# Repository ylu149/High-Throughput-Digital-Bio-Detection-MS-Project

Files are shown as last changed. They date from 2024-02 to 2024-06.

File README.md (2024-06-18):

# Automated High-Throughput Virus Detection System

## Project Demo
https://drive.google.com/file/d/1OpM7CCfLptdZOMjBMuT8S1R-RPZTFUh5/view?usp=sharing

## Introduction

In response to the growing threat of infectious diseases and viruses, especially in the post-COVID-19 era, there is an urgent need for cost-effective, multiplexed, label-free, high-throughput virus detection methods for small single samples. This project aims to design and prototype an automated system that can seamlessly transport and center a standardized microtiter plate's wells in front of a stationary Interferometric Reflectance Imaging Sensor (IRIS) optical system. The system facilitates high-throughput digital measurements of distinct binding events within each well, providing unprecedented sensitivity and resolution.

## Goals Outlined

The project is divided into three phases: research, prototyping, and testing. The research phase involves studying methods for positioning microtiter plates and exploring techniques for inserting IRIS chips into the plates. The findings are then used to create a 3D model of the design using SolidWorks. The prototyping phase optimizes the CAD model based on feedback and constructs a proof of concept. Finally, the testing phase focuses on reliability testing of the prototype assembly, including repeatability tests for plate positioning and evaluating the consistency of the dipping mechanism.

## Proposed Design

The proposed design integrates two systems: an XY positioning system and a dipping mechanism.

### XY Positioning System

The XY positioning system uses two pairs of rails and non-capacitive stepper motors to move a 96-well microtiter plate with high precision. The motors push the plate along two perpendicular axes, allowing the IRIS optical system to focus on the selected well. 

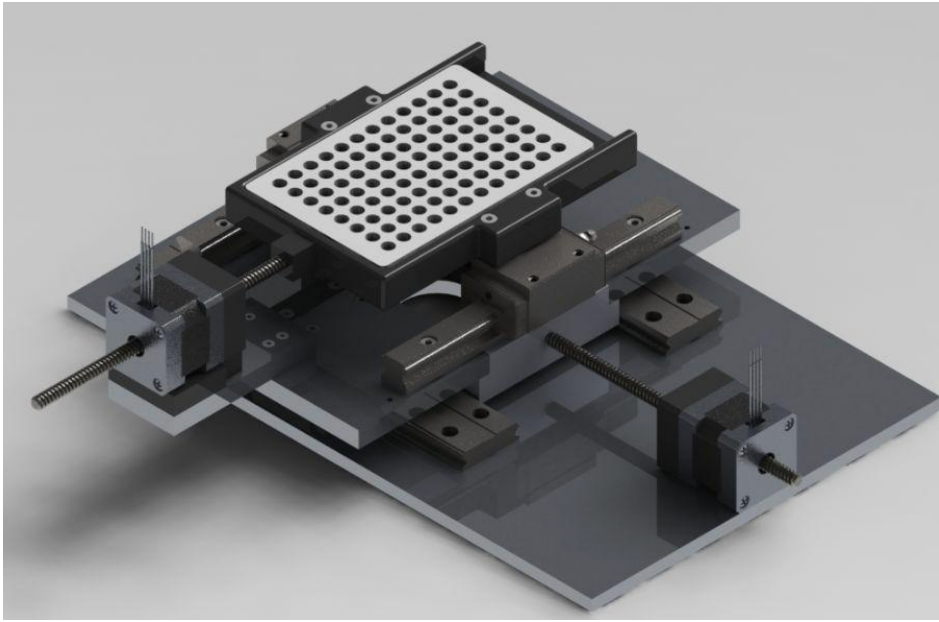
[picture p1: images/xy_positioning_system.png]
XY Positioning System


### Dipping Mechanism

The dipping mechanism facilitates the insertion and cleaning of IRIS chips in the microtiter plate. A specialized part called the "buckle" holds the IRIS chip and is attached to a 3D-printed holder with eight buckles, each equipped with springs to provide a cushion when the IRIS chip contacts the microtiter plate. A linear actuator facilitates the insertion and retraction of the IRIS chips. The entire assembly is illustrated below.

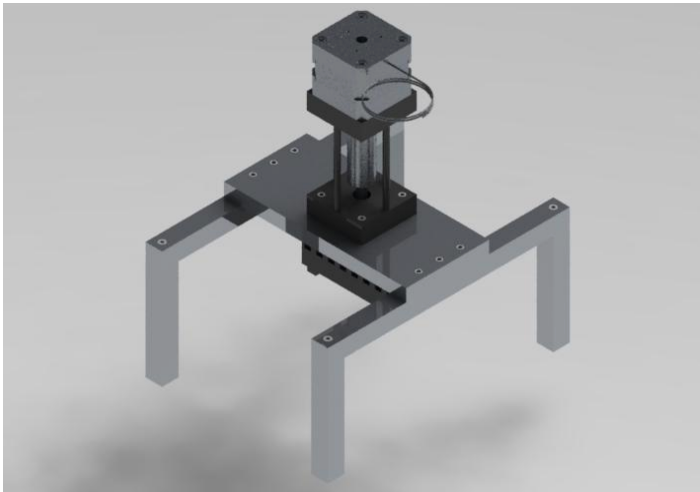
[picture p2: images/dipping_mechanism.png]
Dipping Mechanism


## Cleaning IRIS Chips

To clean the IRIS chips, half of the wells in the microtiter plate are designated for cleaning, while the other half is used for sampling. This arrangement allows the system to sequentially sample eight samples in a column, clean itself, and then proceed to resample.

## System Overview

The complete system, comprising the XY positioning system and dipping mechanism, is depicted below.

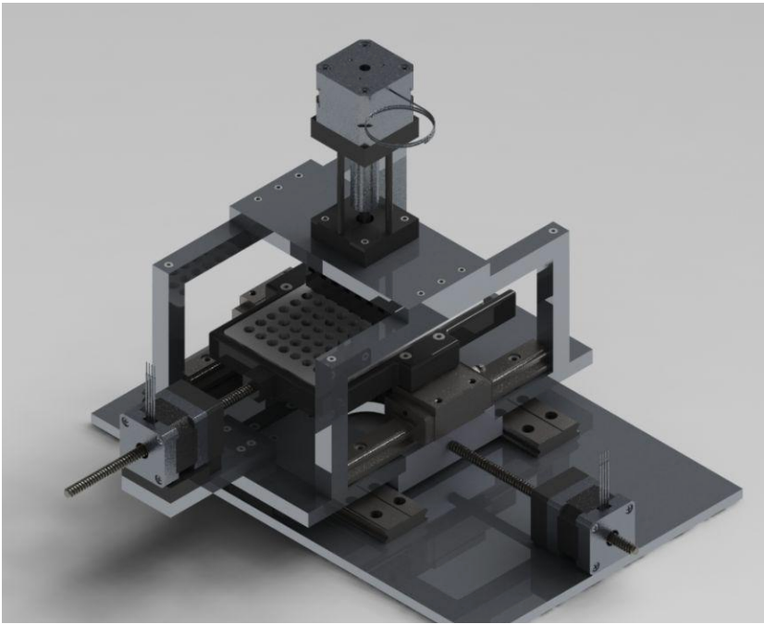
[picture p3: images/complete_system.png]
Complete System


## Arduino Wiring Diagram
The electrical system showing how the stepper motors are wired is shown below. Note each stepper motor, gets it's own Arduino and driver. 

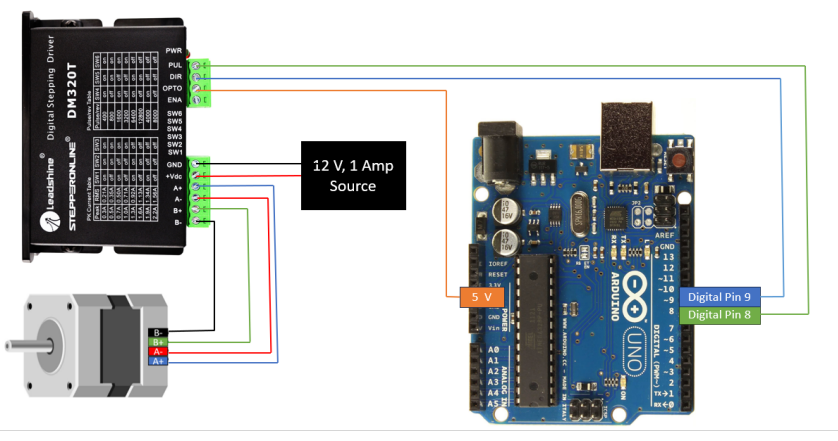
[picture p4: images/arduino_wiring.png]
Wiring Diagram


## Credits
- Harisson Cao: For being my partner throughout this project. 
- Andrew Gentile: For providing feedback as an engineer in industry. 
- The anonymous machinist who helped machine parts and gave GD&T feedback.
- Selim Unlu: For being the advising professor on this project.
- Mete Aslan: For the feedback he provided as a PhD student.  

## For more detailed explanations please refer to the report.pdf and BOM.XLSX documents.

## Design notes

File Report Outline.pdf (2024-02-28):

## Boston University College of Engineering Department of Electrical and Computer Engineering

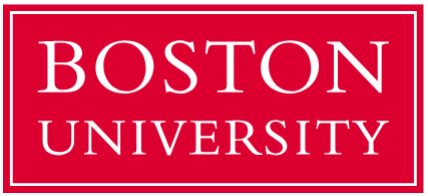
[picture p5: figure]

## High-Throughput Digital Biodetection

## Master’s Project End of Semester Report

## Harrison Cao & Yang Zeng Lu

## Advisor: Professor M. Selim Ünlü

## December 15th

, 2023

## Table of Contents

### I. Introduction | 3

### II. Goals Outlined | 3

### III. Proposed Design... | 4

### IV. Testing & Results | 8

### V. Conclusion | 10

### VI. Appendix | 12

### I. Introduction

Considering the growing threat posed by infectious diseases and viruses, particularly in light of

the post-Covid-19 era, there is an urgent and pressing need for cost-effective multiplexed, label-free,

high-throughput virus detection methods for small single samples. One emerging method for single

molecule detection involves harnessing optics through Interferometric Reflectance Imaging Sensors (IRIS

chips) to precisely gauge the size and quantity of particles within individual samples.

The objective of this project is to design and prototype an automated system capable of

seamlessly transporting and centering a standardized microtiter plate’s wells in front of a stationary IRIS

optical system. This system will facilitate high-throughput digital measurements of distinct binding events

within each well of a microtiter plate during the sample incubation process. This innovative approach

unlocks unprecedented capabilities in high-throughput digital bio-sensing, offering levels of sensitivity

and resolution that surpass traditional labeling methods.

### II. Goals Outlined

During the initial project proposal, the approach and subsequent goals were divided into three

phases: research, prototyping, and testing. In the research phase, various methods for positioning 96-well

microtiter plates while minimizing vibration were studied. Different techniques for inserting IRIS chips

into the 96-well microtiter plates were also explored. The concepts derived from this research were then

used to create a 3D model of the design using SolidWorks. During the prototyping phase, we optimized

the CAD model based on feedback received. This optimized design was then constructed as a proof of

concept. Finally, in the testing phase, we focused on the reliability testing of the prototype assembly. This

involved conducting repeatability tests for positioning the microtiter plates along two different axes and

evaluating the consistency of our dipping mechanism.

### III. Proposed Design

The proposed design for this project involves two systems integrated together. These systems

include a XY positioning system and the dipping mechanism.

The objective of the XY positioning system is to move a 96-well microtiter plate with high

precision and accuracy from well to well. Specifically, the system should position a designated well, as

selected by the user, to a focal point in a 2D space. This positioning enables the IRIS optical system to

focus on the selected well.

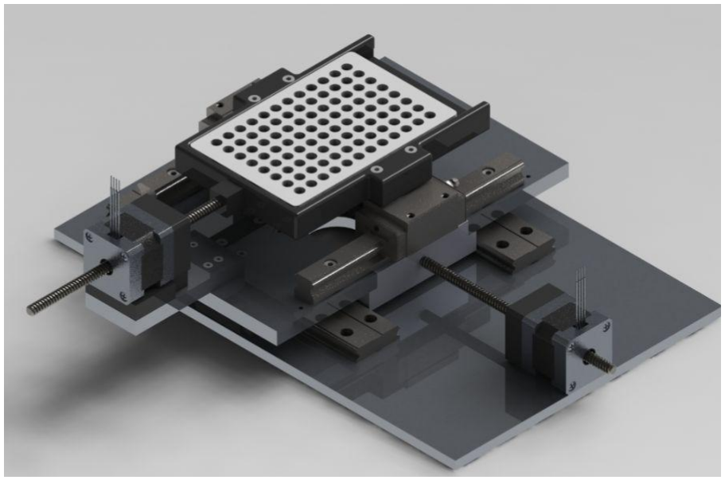
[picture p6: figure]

Figure 1: 3D Render of XY Positioning System in SolidWorks

The proposed design for positioning the microtiter plate uses two pairs of rails and two

non-capacitive stepper motors. These motors will position the microtiter plates by pushing them along

two perpendicular axes, with each axis having its own set of rails. By pushing the well plate only from its sides, it is ensured that the bottom of the wells remains unobstructed. This design allows the IRIS optics

system to capture the individual wells of the microtiter plate as the positioning system moves the plate.

Additionally, an Arduino, alongside a stepper motor driver, will be used to control the

non-capacitive stepper motors. The wiring diagram for this setup is shown in figure 2. The pseudo-code

for driving the stepper motor can be found in the appendix.

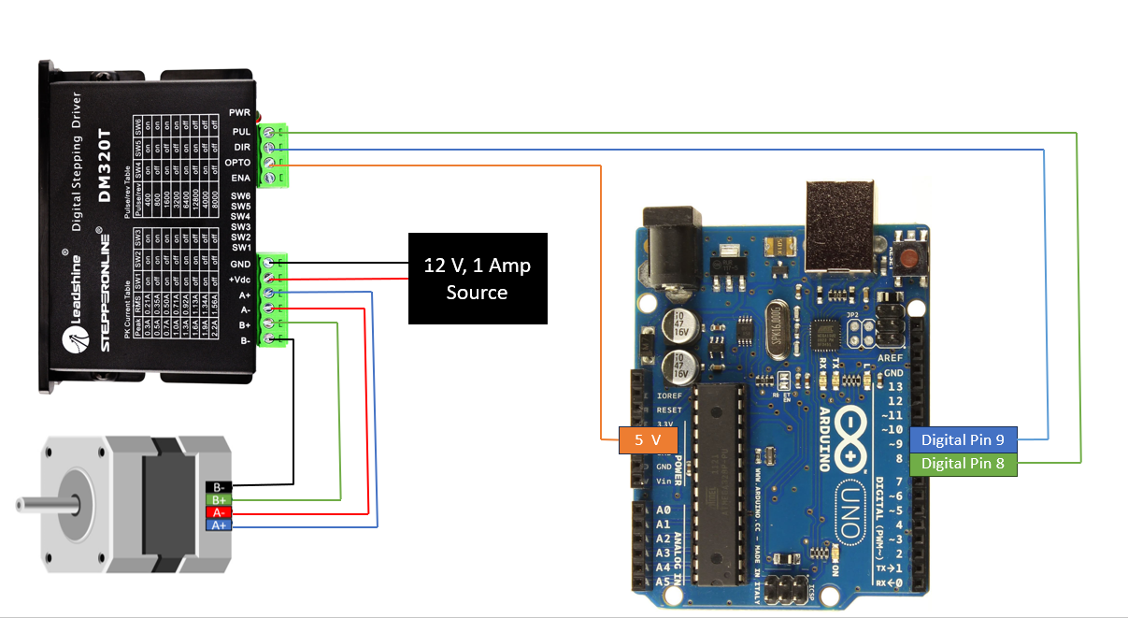
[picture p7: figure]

Figure 2: Wiring diagram for Arduino, stepper motors, and stepper motor drivers

To facilitate the insertion and cleaning of IRIS chips in a microtiter plate for the IRIS optical

system, a specialized dipping mechanism needed to be designed. This mechanism ensures the IRIS chips

are held securely and make direct contact with the base of the microtiter plate, without causing damage to

either component. The IRIS chip must be positioned no more than 0.5 mm from the inside glass surface of

the well plate for the optical system to function effectively. Additionally, to prevent cross-contamination

between samples, a cleaning method for the IRIS chips after each sample is necessary.

Addressing these requirements, the proposed solution involves a resin-printed part called the

"buckle," to which the IRIS chip will be friction-fitted to. This buckle will then be attached to a

3D-printed holder alongside eight other buckles, each equipped with springs. These springs provide a 2

mm cushion when the IRIS chip contacts the microtiter plate, protecting the glass at the bottom of the

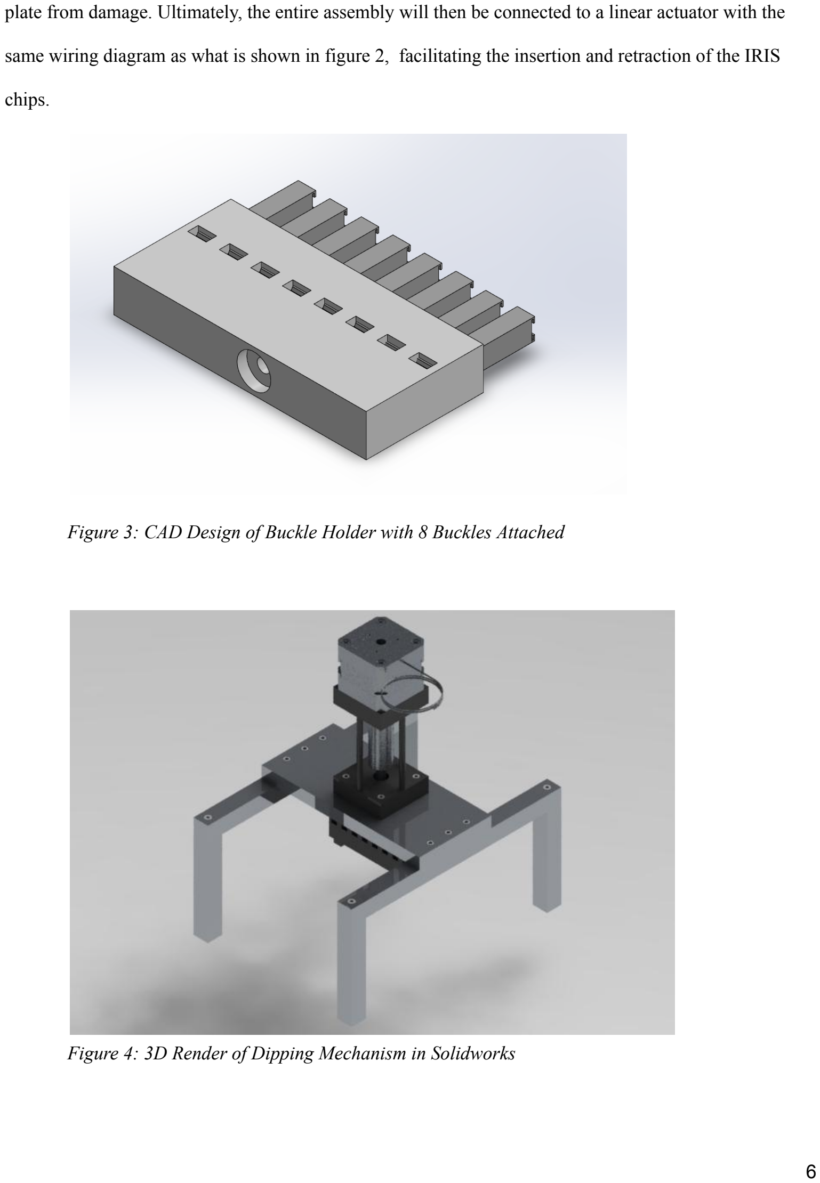
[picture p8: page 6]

plate from damage. Ultimately, the entire assembly will then be connected to a linear actuator with the

same wiring diagram as what is shown in figure 2, facilitating the insertion and retraction of the IRIS

chips.

Figure 3: CAD Design of Buckle Holder with 8 Buckles Attached

Figure 4: 3D Render of Dipping Mechanism in Solidworks

For cleaning the IRIS chips, it's proposed that half of the wells in the microtiter plate be

designated for cleaning, while the other half are used for sampling. This arrangement allows the device to

sequentially sample eight samples in a column, clean itself, and then proceed to resample.

Ultimately, our entire system is shown below in figure 5. A bill of materials can be found in the

Appendix

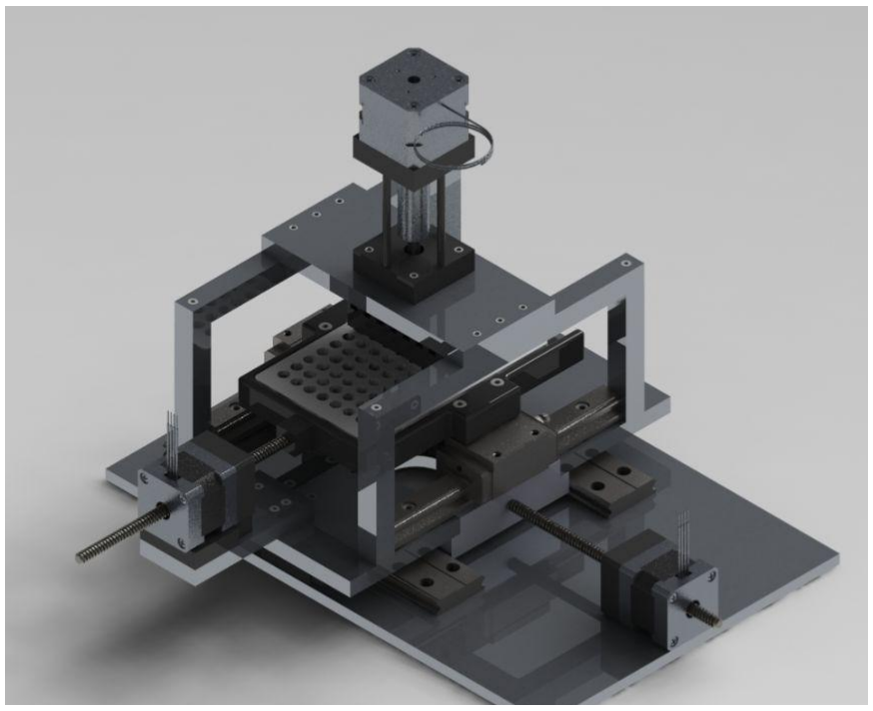
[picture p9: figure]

Figure 5: 3D Render of the XY Positioning and Dipping System in SolidWorks

### IV. Testing & Results

To evaluate the precision and accuracy of the XY positioning system, each axis was assessed

independently. The x-axis, controlled by the stepper motor pushing on the shorter edge of the microtiter

plate, determines the positioning of rows, labeled A-F. Conversely, when the motor pushes along the

longer edge or the y-axis, it positions the columns of the microtiter plate, each labeled with a number

labeled 1-12.

For specific cell positioning tests on the microtiter plate, the X and Y axes were individually

examined using a consistent method. Regarding the X-axis, an arbitrary zero point was established to

align row A with the hole for the optical system. After setting this point, the distance traveled between

rows was measured ten times. The process involved commanding the stepper motor to move sequentially

from row A to H. Upon reaching row H, the plate returned to A for repeated measurements. These tests

were conducted ten times, and the resulting data was used to calculate the standard deviation, reflecting

the precision of the X-axis positioning system. For accuracy assessment, the average deviation from each

row was determined. This value, along with the known 9 mm ground truth value, was used to calculate

the average percentage error. Please refer to table 1 below for the values. Overall, there is less than a 0.1

mm standard deviation and less than 2% error for moving the stepper motor.

Rows | A | B | C | D | E | F | G | H
Average (mm) | 19.51 | 28.51 | 37.53 | 46.447 | 55.36 | 64.32 | 73.17 | 82.14
Standard Deviation (mm) | 0.077 | 0.044 | 0.040 | 0.047 | 0.053 | 0.078 | 0.088 | 0.079
Average Percent Error | - | 0.02 | 0.17 | 0.87 | 0.94 | 0.47 | 1.6 | 0.40

Table 1: X-axis stepper motor data, showing the mean, standard deviation, and percent error averaged across 10 iterations.

The Y-axis positioning was evaluated in a very similar way to the X-axis. The only difference is

that the Y-axis stepper motor is numbered from 1-12 rather than labeled A-H. The data for the Y-axis is

shown in table 2.

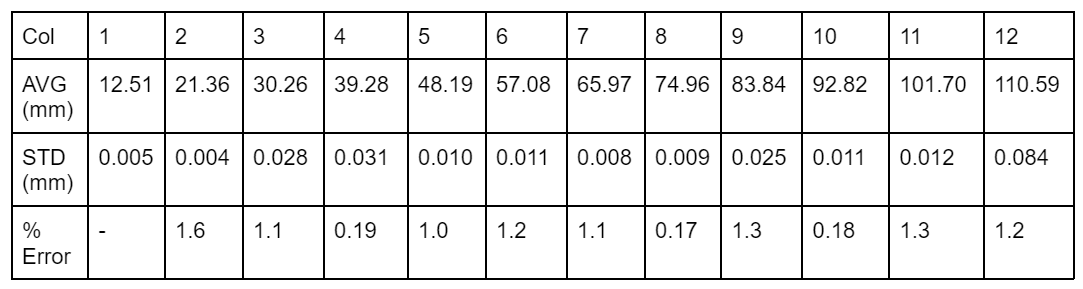
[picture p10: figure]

Table 2: Y-axis stepper motor data, showing the mean, standard deviation, and percent error averaged across 10 iterations.

In terms of the dipping mechanism used for inserting iris chips, measuring the tolerances of each

buckle is extremely difficult. Consequently, we conducted a pass-fail test to validate the consistency of

the mechanism. The design successfully passed 10 iterations of repeated dipping across columns 1 to 12

without any issues. However, it's important to note that the dipping mechanism requires significant

fine-tuning before it can achieve consistent performance. This need arises from the mounting

mechanism's design, which connects the buckle housing to the stepper motor. Currently, there's free

rotational motion, as nothing is preventing the buckle holder from rotating. This issue, which will be

discussed further in the conclusion section, will need to be improved.

### V. Conclusion

All the goals outlined in our initial proposal have been largely achieved. During the research

phase, we iterated multiple times and finalized a design for the XY positioning and IRIS chip dipping

mechanism. This led to the development of a 3D model defining the prototype. In the prototyping phase,

the CAD model was brought to life through machining and 3D printing. Subsequently, in the testing

phase, we conducted several reliability tests on the prototype. The primary shortfall, however, lies in

integrating the prototype with the IRIS optical system. Due to our limited experience in machining, this

process was more time-consuming than anticipated, delaying most testing and adjustments until recently.

For improvement, several aspects need attention. Currently, the electronics are operated using

three Arduinos to simplify wiring and isolate testing conditions. Ideally, this should be streamlined to a

single controller managing all three stepper motors, reducing costs and potential failure points.

Additionally, the placement of the electronics was not considered in the design phase. They are currently

attached to the prototype with adhesive. Incorporating additional tapped holes on the base plate would

allow the electronics to be securely bolted down and covered, minimizing hazards. Moreover, the dipping

mechanism's positioning relies on manual adjustment by the user and has nothing to prevent it from

rotating. Designing a guide would ensure correct placement without user adjustments and prevent free

rotation. Finally, the machined aluminum parts could benefit from remanufacturing with tighter tolerances

and improved surface finishes for enhanced quality.

As this project comes to an end, we'd like to reflect on some key takeaways and lessons learned.

First and foremost, we learned the importance of not underestimating any aspect of a project. Initially, we

believed this project would be straightforward and moderately challenging. However, as we delved

deeper, we quickly realized the complexity was far greater than anticipated. This led to certain goals

becoming more time-consuming and demanding than we had expected. Consequently, a significant lesson

for us was the need to avoid overpromising. As we progressed, it became clear that what we had thought

feasible within our timeline required much more effort and resources. Despite successfully achieving most of our objectives, we found ourselves in a constant race against time. This experience has taught us

the value of realistic planning and setting achievable milestones. It has also highlighted the importance of

flexibility and adaptability in managing complex projects, especially when faced with unexpected

challenges. Looking back, these insights have not only enhanced our technical skills but also enriched our

understanding of effective project management.

### VI. Appendix

Bill of Materials

ITEM NO. | PART NUMBER | DESCRIPTION | QTY.
1 | 9057K16 | Base Plate Everything is mounted to, Tight-Tolerance Multipurpose 6061 Aluminum with Certificate | 1
2 | 14N21xx_1.STEP | The NEMA 14 Stepper Motors used in the XY positioning system | 2
3 | Stepper_motor_hold er | 3D Printed Part Responsible for holding the X Axis Stepper Motor and Base Plate together when screwed in | 1
4 | X_Carriage_Adapter _Plate_one_carriage | Adapter Plate for the X Direction Carriages, nearly everything is mounted onto here | 2
5 | 6382K111 | 33 mm Wide x 190 mm Long Guide Rail for Extra-Wide Ball Bearing Carriage | 2
6 | 6382K21_Extra-Wide Ball Bearing Carriage | Extra-Wide Ball Bearing Carriage | 2
7 | 92855A408 | 18-8 Stainless Steel Low-Profile Socket Head Screws | 3
8 | Dipping_support | The short support legs of the Dipping Mechanism | 4

9 | Dipping_base | The Long supports the Dipping Adapter Plate sits on | 2
10 | 92855A316 | 18-8 Stainless Steel Low-Profile Socket Head Screws | 27
11 | 92855A410 | 18-8 Stainless Steel Low-Profile Socket Head Screws | 8
12 | 91290A164 | Alloy Steel Socket Head Screw | 4
13 | microwellPlateHolde rFinalRev (1) | Holder for the 96 Well Microtiter Plate | 1
14 | 6709K301 | 15 mm Wide x 160 mm Long Guide Rail for Ball Bearing Carriage | 2
15 | 6709K12_Ball Bearing Carriage | Ball Bearing Carriage | 2
16 | microtierplatetruedi m | Model of the 96 Well Microtiter Plate | 1
17 | 90666A117 | Super-Corrosion-Resistant 316 Stainless Steel Socket Head Screw | 4
18 | X_Adapter_Bar_Push | Linch Pin Piece, responsible for connecting both X Adapter Plates | 1
19 | Y_Stepper_Block | 3D Printed Block that Y Stepper Motor is placed on | 1
20 | Stepper_motor_hold er_Y_axis | 3D Printed Part Responsible for holding the Y Adapter and Stepper motor together when screwed in | 1

21 | Y_stepper_motor_ad apter_plate | Adapter Plate for the Y-Axis Stepper Motor | 1
22 | 4290N12 | Compact Stepper Motor Actuator Used in Dipping | 1
23 | actuatorMount | | 1
24 | 92196A110 | 18-8 Stainless Steel Socket Head Screw | 4
25 | dipping_adapter_pl ate | Adapter Plate for the Dipping Mechanism | 1
26 | 92196A023 | 18-8 Stainless Steel Socket Head Screw | 10
27 | Buckle_Holder_8_dip | Holder for the "Buckles" | 1
28 | buckle2mm_7mm_l_ 1mm_hang | "Buckles", holder for the IRIS Chips | 8
29 | Arudino UNO R3 | Microcontrollers responsible controlling the logic of the stepper motors | 3
30 | StepperOnline DM 320T | An interface that connects the stepper motor with the Arduino | 3

Arduino Pseudocode for Positioning along X and Y Axis:
Import the Stepper.h library

Initialize constants:
- stepsPerRevolution: [Specify the number of steps per revolution for your motor]
- stepDistance: [Specify the distance covered per step, in millimeters]

Initialize the stepper motor:
- Use Pin 8 as the pulse (PUL) pin
- Use Pin 9 as the direction (DIR) pin

Create stepper motor object with stepsPerRevolution, Pin 8, and Pin 9

Setup:
- Set the speed of the stepper motor to the desired RPM
- Initialize serial communication with the desired baud rate

Loop:
- Check if there is serial input available
- If input is available:
- Read the input and check if it is a letter between 'A' and 'H' or positions 1-12
- Convert letter to a corresponding position if needed:
- Map 'A' to position 0, 'B' to position 1, ..., 'H' to position 7
- Calculate the distance to move:
- Each position corresponds to a movement of 9mm
- Calculate the number of steps to move using the formula: steps = mmToSteps(9 * (targetPosition -currentPosition))
- Move the stepper motor by the calculated steps
- Update the current position to the new position

Function mmToSteps(mm):
- Convert the distance in millimeters to steps using the formula: return round(mm / stepDistance)

[Optional]
Function for stepper movement:
- Define a function to handle the movement of the stepper motor

Arduino Pseudocode for Dipping Mechansim

Include Stepper library

Define constants:
- stepsPerRevolution: 400 (Number of steps per revolution of the motor)
- stepDistance: 0.00396875 inches (Distance covered by the motor per step)

Initialize stepper motor object (myStepper) with stepsPerRevolution, Pin 8 for pulse, and Pin 9 for direction

Setup Function:
- Set the speed of myStepper to 500 RPM
- Initialize serial communication at 9600 baud rate
- Flush the serial communication to clear any existing data

Define steps as the number of steps for a 1mm movement using mmToSteps function Define iters as 6 (number of iterations for the movement)

Loop Function:
- Check if the user presses 'y' to move the stepper motor down
- If yes, call runner function with iters and -steps (to move down)
- Wait for 1 second (delay)
- Check if the user presses 'y' to move the stepper motor up
- If yes, call runner function with iters and steps (to move up)
- Wait for 1 second (delay)

Function mmToSteps(mm):
- Calculate mmPerStep as stepDistance converted to millimeters (1 inch = 25.4 mm)
- Return the number of steps for the given mm distance, rounded to the nearest integer

Function runner(iterations, steps):
- Repeat for the number of iterations:
- Move the stepper motor by the given number of steps

Function promptUser(expectedChar):
- Prompt the user to press a specified character (expectedChar) to move the stepper motor
- Keep checking for serial input indefinitely
- If the expected character is received, return true

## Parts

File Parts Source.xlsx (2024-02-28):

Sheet: Most up to Date
 | Item | Price | Quanity | Total Price | Link
(Purchased) 11/4/2023 | Extra-Wide Ball Bearing Carriage for 33 mm Wide Rail | $189.29 | 2 | $378.58 | https://www.mcmaster.com/6382K21/
(Purchased) 11/4/2023 | 190 mm Long, 33 mm Wide Guide Rail for Extra-Wide Ball Bearing Carriage | $138.70 | 2 | $277.40 | https://www.mcmaster.com/6382K11-6382K111/
(Purchased) 11/4/2023 | Ball Bearing Carriage for 15 mm Wide Rail | $118.97 | 2 | $237.94 | https://www.mcmaster.com/6709K12/
(Purchased) 11/4/2023 | 15 mm Wide Guide Rail for Ball Bearing Carriage | $51.20 | 2 | $102.40 | https://www.mcmaster.com/6709K33-6709K301/
(Purchased 2) 11/4/2023 | Arduino Uno | $27.89 | 3 | $83.67 | https://www.amazon.com/Arduino-A000066-ARDUINO-UNO-R3/dp/B008GRTSV6?hvadid=309751315916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
(Purchased) 11/4/2023 | NEMA 14 NON-CAPTIVE LINEAR ACTUATOR | $129.00 | 2 | $258.00 | https://dingsmotionusa.com/store/nema-14-non-captive-linear-actuator
(Purchased) 11/28/2023 | 90666A117, Super-Corrosion-Resistant 316 Stainless Steel Socket Head Screw, Low-Profile, M4 x 0.7 mm Thread, 20 mm Long (Pack of 50) | $12.88 | 1 | $12.88 | https://www.mcmaster.com/90666A117/
(Purchased) 11/28/2023 | 92855A410, 18-8 Stainless Steel Low-Profile Socket Head Screws, with Hex Drive, M4 x 0.7 mm Thread, 10 mm Long (Pack of 50) | $6.90 | 1 | $6.90 | https://www.mcmaster.com/92855A410/
(Purchased) 11/28/2023 | 92855A316, 18-8 Stainless Steel Low-Profile Socket Head Screws, with Hex Drive, M3 x 0.5 mm Thread, 16 mm Long (pack of 25) | $4.43 | 2 | $8.86 | https://www.mcmaster.com/92855A316/
(Purchased) 11/28/2023 | 92855A408, 18-8 Stainless Steel Low-Profile Socket Head Screws, (pack of 25) with Hex Drive, M4 x 0.7 mm Thread, 8 mm Long | $8.05 | 1 | $8.05 | https://www.mcmaster.com/92855A408/
(Purchased) 11/28/2023 | 91290A164, Alloy Steel Socket Head Screw, Black-Oxide, M4 x 0.7 mm Thread, 18 mm Long, (pack of 100) | $15.38 | 1 | $15.38 | https://www.mcmaster.com/91290A164/
(Purchased) 11/28/2023 | 9057K16, Tight-Tolerance Multipurpose 6061 Aluminum with Certificate, Precision Ground on All Sides, 8" x 12", 1/4" Thick | $106.10 | 1 | $106.10 | https://www.mcmaster.com/9057K16/
(Purchased) 11/28/2023 | 4290N12, Compact Stepper Motor Actuator, NEMA 17, 0.00015625" Travel Distance Per Full Step | $221.11 | 1 | $221.11 | https://www.mcmaster.com/4290N12/
(Purchased) 11/28/2023 | 92196A111, 18-8 Stainless Steel Socket Head Screw, 4-40 Thread Size, 9/16" Long (Pack of 100) | $6.64 | 1 | $6.64 | https://www.mcmaster.com/92196A110/
(Purchased) 11/28/2023 | 92196A023, 18-8 Stainless Steel Socket Head Screw, 4-40 Thread Size, 11/16" Long (Pack of 10) | $13.33 | 2 | $26.66 | https://www.mcmaster.com/92196A023/
(Purchased 2) | DM320T, Digital Stepper Driver 0.3-2.2A 10-30VDC for Nema 8, 11, 14, 16, 17 Stepper Motor | $12.51 | 3 | $37.53 | https://www.omc-stepperonline.com/digital-stepper-driver-0-3-2-2a-10-30vdc-for-nema-8-11-14-16-17-stepper-motor-dm320t
(Purchased) 11/28/2023 | Arduino Uno Cable | $9.99 | 3 | $29.97 | https://www.amazon.com/USB-2-0-Interface-Keyboard-Microphone-Instrument/dp/B01BIE98PO
 |  | Total Cost | $1818.07
 |  | Screw Cost | $122.90

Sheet: Ignore this sheet
Item | Price | Quanity | Total Price | Link
Extra-Wide Ball Bearing Carriage for 33 mm Wide Rail | $189.29 | 4 | $757.16 | https://www.mcmaster.com/6382K21/
310 mm Long, 33 mm Wide Guide Rail for Extra-Wide Ball Bearing Carriage | $226.30 | 4 | $905.20 | https://www.mcmaster.com/6382K11-6382K26/
Dipping Mechanism Actuator (PA-07, 12 V DC, 4 inch stroke) | $70.00 | 1 | $70.00 | https://www.progressiveautomations.com/products/micro-linear-actuator
Y-Direction Actuator (PA-04-HS, 12 V DC, 6 inch stroke) | $176.00 | 1 | $176.00 | https://www.progressiveautomations.com/products/hall-effect-sensor-actuator
X-Direction Actuator (PA-04-HS, 12 V DC, 10 inch stroke) | $176.00 | 1 | $176.00 | https://www.progressiveautomations.com/products/hall-effect-sensor-actuator
MegaMoto Plus H-bridge for Arduino (LC-80) | $66.00 | 2 | $132.00 | https://www.progressiveautomations.com/products/lc-80
Arduino Uno | $27.89 | 2 | $55.78 | https://www.amazon.com/Arduino-A000066-ARDUINO-UNO-R3/dp/B008GRTSV6?hvadid=309751315916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
Aluminum stock 1x12x0.25 in | $45.21 | 3 | $135.63 | https://www.mcmaster.com/9057K176/
Aluminum stock 12x12x.5 in | $566 | 1 | $566 | https://www.mcmaster.com/9057K488/
Aluminum Stock 6x6x1 | $103.21 | 2 | $206.42 | https://www.mcmaster.com/9057K68/
Extraneous (screws, extra aluminum needed, 3D printing costs, cables, etc.) |  |  | $500
Total Cost Approximate |  |  | $3680.19
https://www.mcmaster.com/9057K182/ | New Carriage
https://www.mcmaster.com/9057K321/ | New Holder block
https://www.mcmaster.com/9057K39/
https://www.mcmaster.com/3511T33/

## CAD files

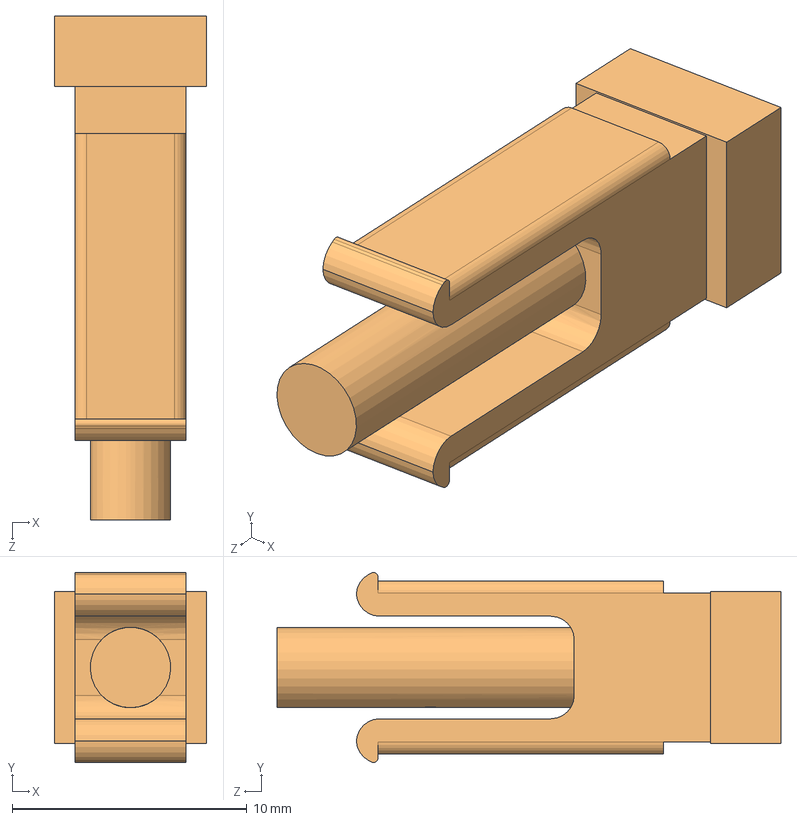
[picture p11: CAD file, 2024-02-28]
PlateReader CAD and DWG/Dipping Mechanism/Dipping_Iris_chip_holder.SLDASM
6.50 x 8.10 x 21.5 mm
buckle
iris_chip_example

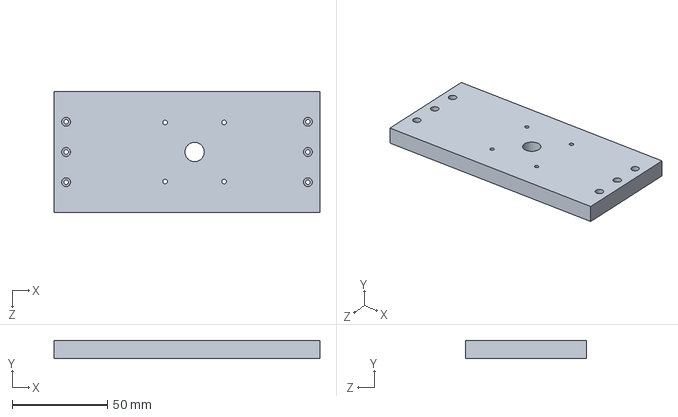
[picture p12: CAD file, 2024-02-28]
PlateReader CAD and DWG/Dipping Mechanism/dipping_adapter_plate.SLDPRT
139.7 x 9.53 x 63.5 mm

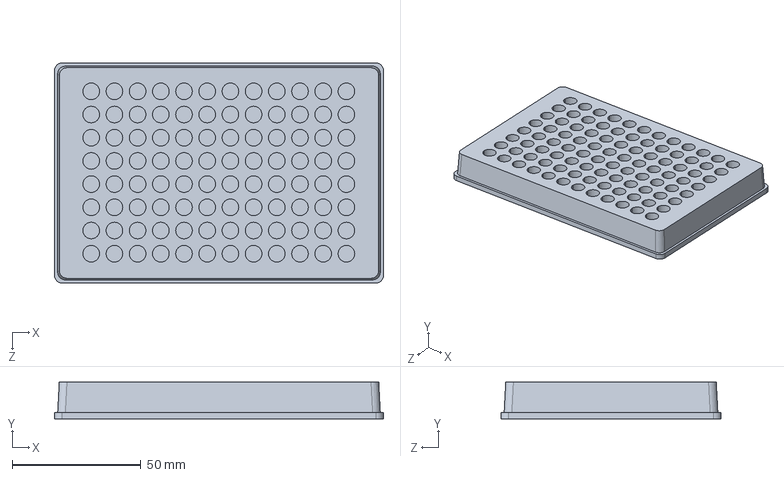
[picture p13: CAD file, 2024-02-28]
PlateReader CAD and DWG/Y Linear Stage/microtierplatetruedim.SLDPRT
127.6 x 14.3 x 85.5 mm

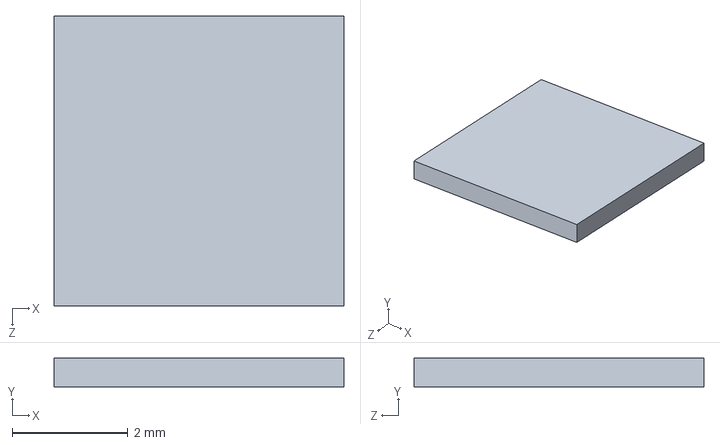
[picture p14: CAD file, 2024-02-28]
PlateReader CAD and DWG/Dipping Mechanism/iris_chip_example.SLDPRT
5.00 x 0.5 x 5.00 mm

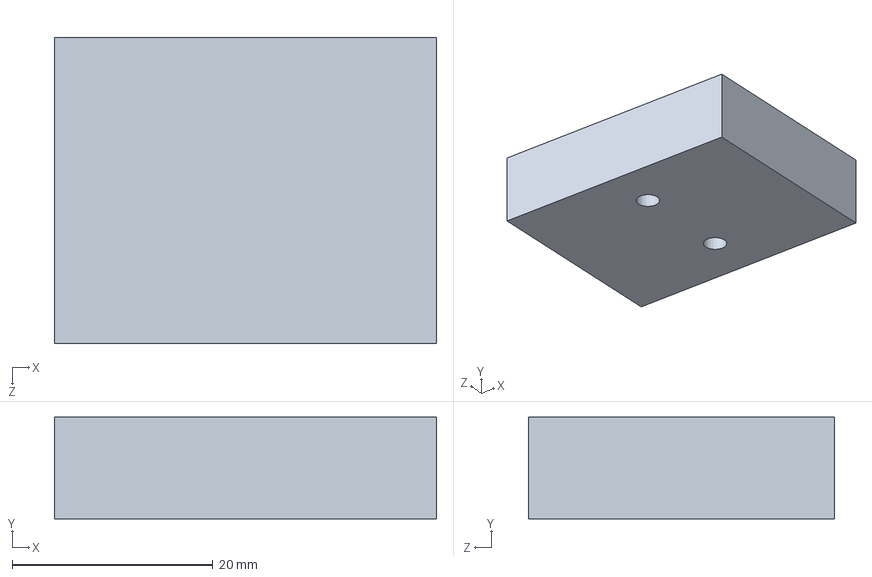
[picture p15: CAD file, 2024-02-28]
PlateReader CAD and DWG/Y Linear Stage/Y_Stepper_Block.SLDPRT
38.1 x 10.2 x 30.5 mm

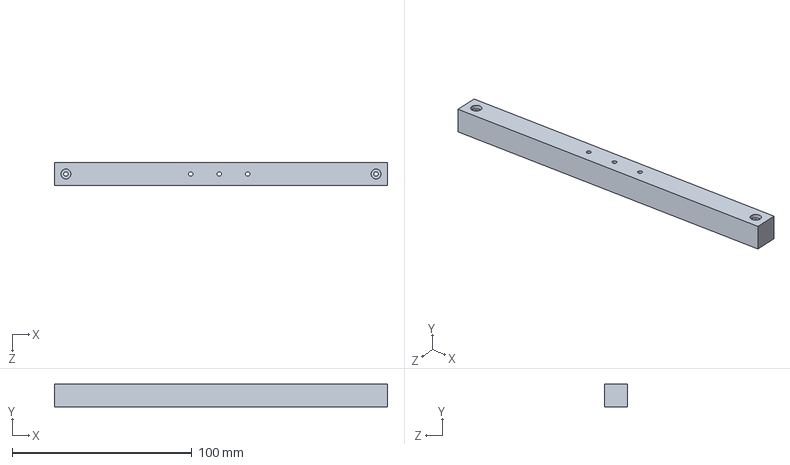
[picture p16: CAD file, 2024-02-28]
PlateReader CAD and DWG/Dipping Mechanism/Dipping_base.SLDPRT
185.4 x 12.7 x 12.7 mm

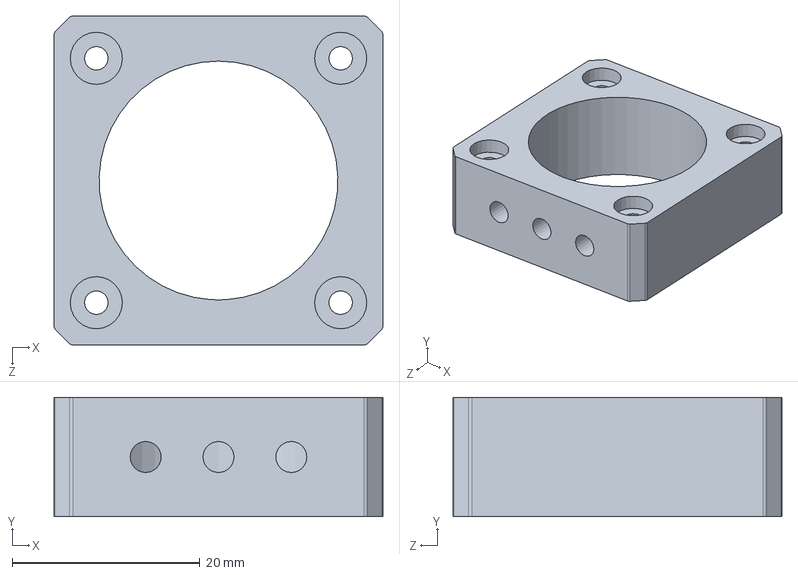
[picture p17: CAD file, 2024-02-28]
PlateReader CAD and DWG/X Linear Stage/Stepper_motor_holder.SLDPRT
35.0 x 12.7 x 35.0 mm

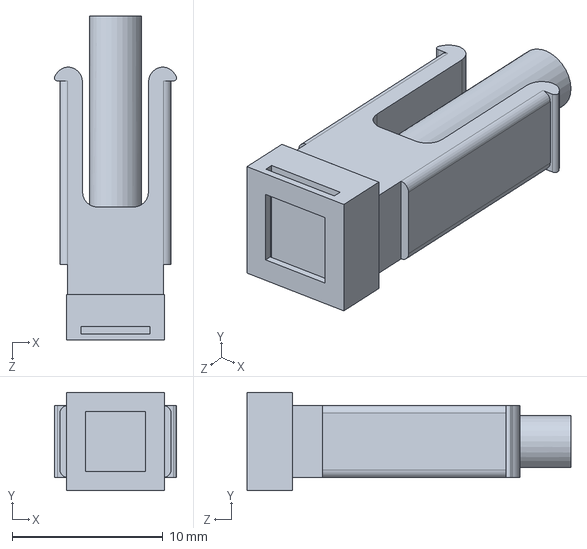
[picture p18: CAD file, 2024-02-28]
PlateReader CAD and DWG/Dipping Mechanism/buckle.SLDPRT
8.10 x 6.50 x 21.5 mm

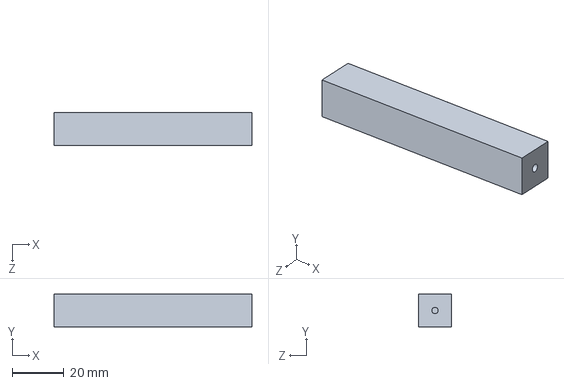
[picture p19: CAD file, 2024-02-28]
PlateReader CAD and DWG/Dipping Mechanism/Dipping_support.SLDPRT
76.2 x 12.7 x 12.7 mm

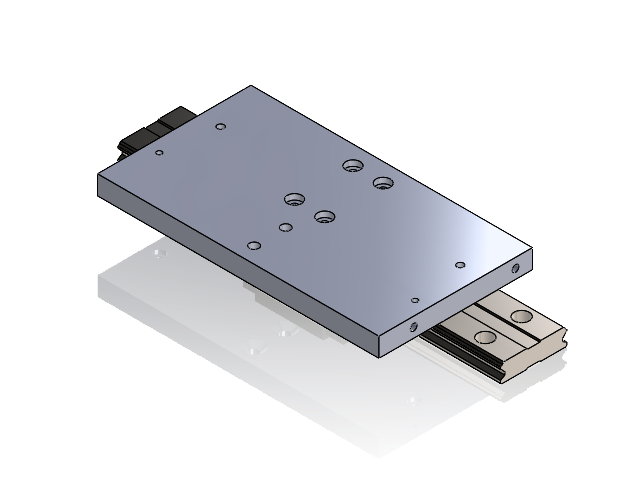
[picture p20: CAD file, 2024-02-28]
PlateReader CAD and DWG/X Linear Stage/X_Stage_one_carriage.SLDASM
X_Carriage_Adapter_Plate_one_carriage
6382K111_33 mm Wide x 190 mm Long Guide Rail for Extra-Wide Ball Bearing Carriage
6382K21_Extra-Wide Ball Bearing Carriage

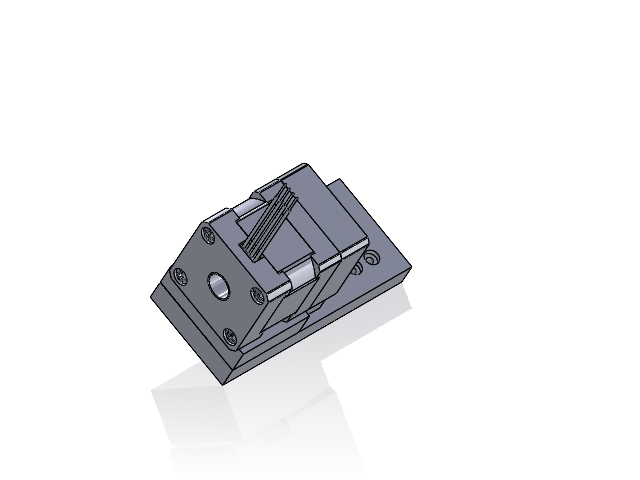
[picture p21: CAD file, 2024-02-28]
PlateReader CAD and DWG/Y Linear Stage/Y_Stepper_Motor.SLDASM
14N Lead Screw.STEP
14N21xx_1.STEP
Y_Stepper_Block
Stepper_motor_holder_Y_axis
Y_stepper_motor_adapter_plate
92855A316_18-8 Stainless Steel Low-Profile Socket Head Screws x 9

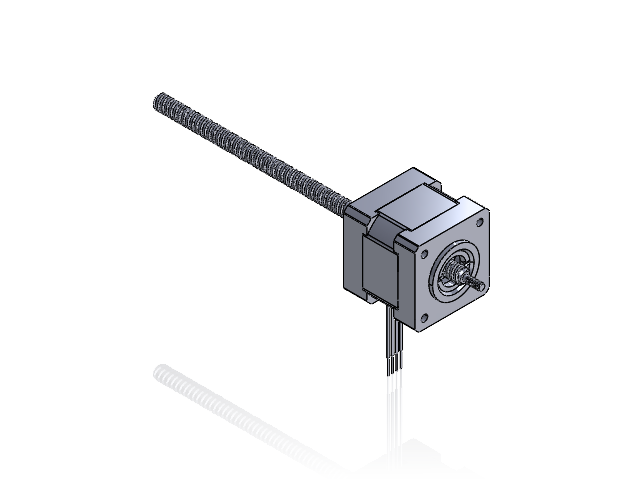
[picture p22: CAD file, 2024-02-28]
PlateReader CAD and DWG/X Linear Stage/14N21xx.STEP.Y_Stage.SLDASM
14N21xx_1.STEP
14N Lead Screw.STEP
Stepper_Screw_Y_Stage

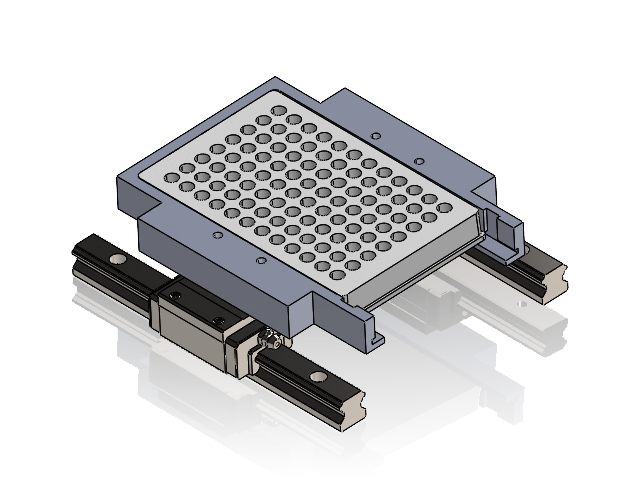
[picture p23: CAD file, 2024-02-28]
PlateReader CAD and DWG/Y Linear Stage/Microplate+Holder.SLDASM
microtierplatetruedim
6709K301_15 mm Wide x 160 mm Long Guide Rail for Ball Bearing Carriage x 2
6709K12_Ball Bearing Carriage x 2
microplateholderv2.stp

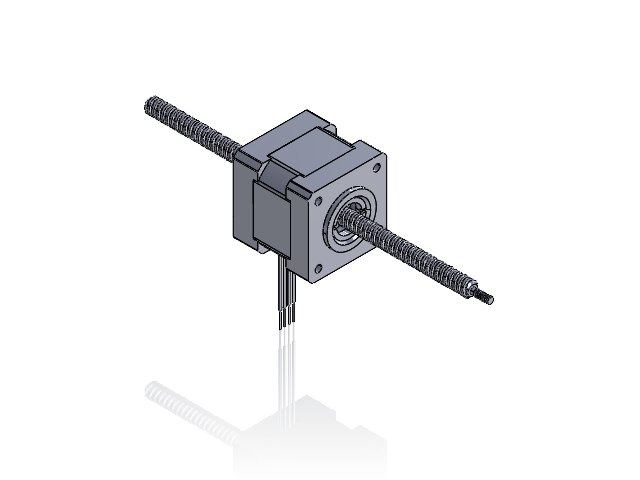
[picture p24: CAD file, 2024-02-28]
PlateReader CAD and DWG/X Linear Stage/14N21xx.SLDASM
14N21xx_1.STEP
14N Lead Screw.STEP

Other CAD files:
PlateReader CAD and DWG/Y Linear Stage/Y_Stage_V2.SLDASM
PlateReader CAD and DWG/X Linear Stage/14N21xx.STEP.SLDASM
PlateReader CAD and DWG/Dipping Mechanism/Buckle holder + 8 buckles.SLDASM
PlateReader CAD and DWG/X Linear Stage/14N21xx_1.STEP.SLDPRT
PlateReader CAD and DWG/Dipping Mechanism/Buckle_Holder.SLDPRT
PlateReader CAD and DWG/Dipping Mechanism/Buckle_Holder_8_dip.SLDPRT
PlateReader CAD and DWG/Dipping Mechanism/Buckle_Holder_8_dip_hole_more_centered_(que89.SLDPRT
PlateReader CAD and DWG/Dipping Mechanism/actuatorMount.SLDPRT
PlateReader CAD and DWG/Dipping Mechanism/buckle2mm_7mm_l_1mm_hang.SLDPRT
PlateReader CAD and DWG/Screws/90666A117_Super-Corrosion-Resistant 316 Stainless Steel Socket Head Screw.SLDPRT
PlateReader CAD and DWG/Screws/91290A144_Alloy Steel Socket Head Screw.SLDPRT
PlateReader CAD and DWG/Screws/91290A164_Alloy Steel Socket Head Screw (1).SLDPRT
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

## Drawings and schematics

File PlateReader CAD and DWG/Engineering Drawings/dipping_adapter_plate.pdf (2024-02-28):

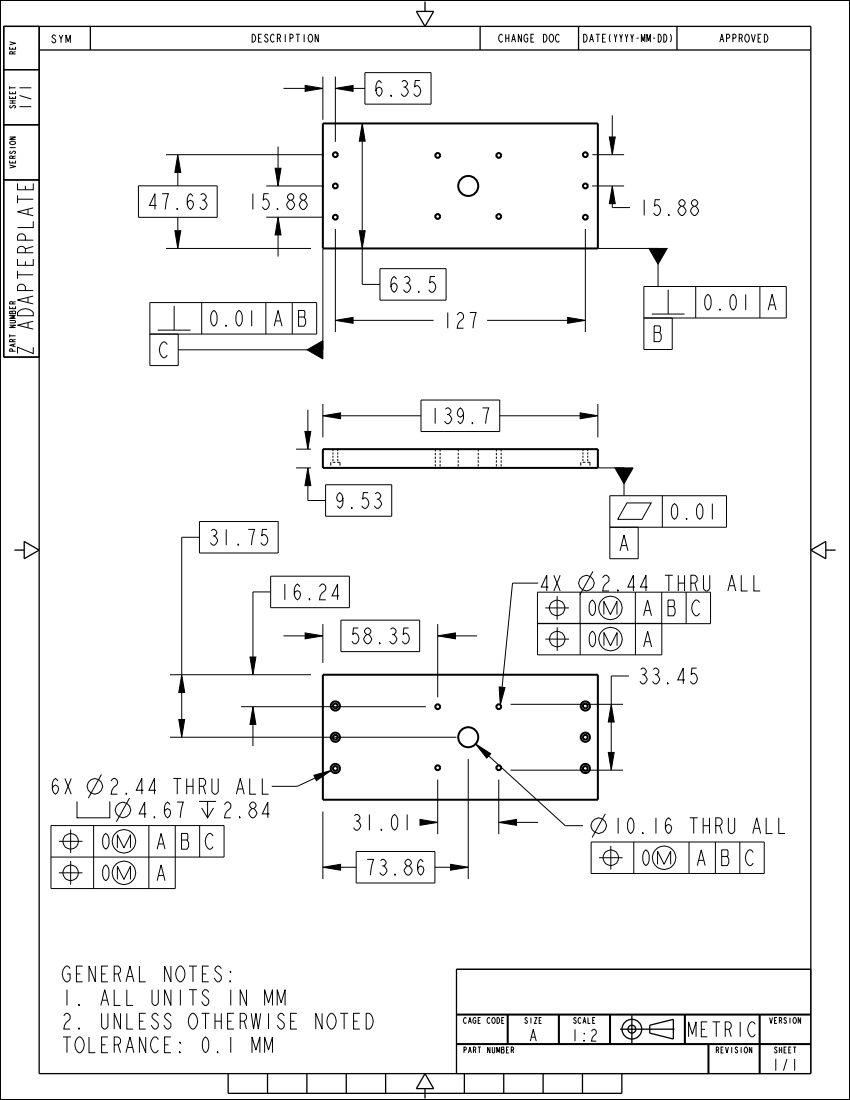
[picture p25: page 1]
SYM; DESCRIPTION; CHANGE; DOC; DATE(YYYY-MM-DD); APPROVED; 10.16 THRU ALL; Z ADAPTERPLATE 1/1; PART NUMBER; REVISION; SHEET; METRIC CAGE; CODE; SIZE; SCALE; VERSION; 6X 2.44 THRU ALL; 4X 2.44 THRU ALL

PART NUMBER VERSION SHEET REV

GENERAL NOTES:
1. ALL UNITS IN MM
2. UNLESS OTHERWISE NOTED
TOLERANCE: 0.1 MM

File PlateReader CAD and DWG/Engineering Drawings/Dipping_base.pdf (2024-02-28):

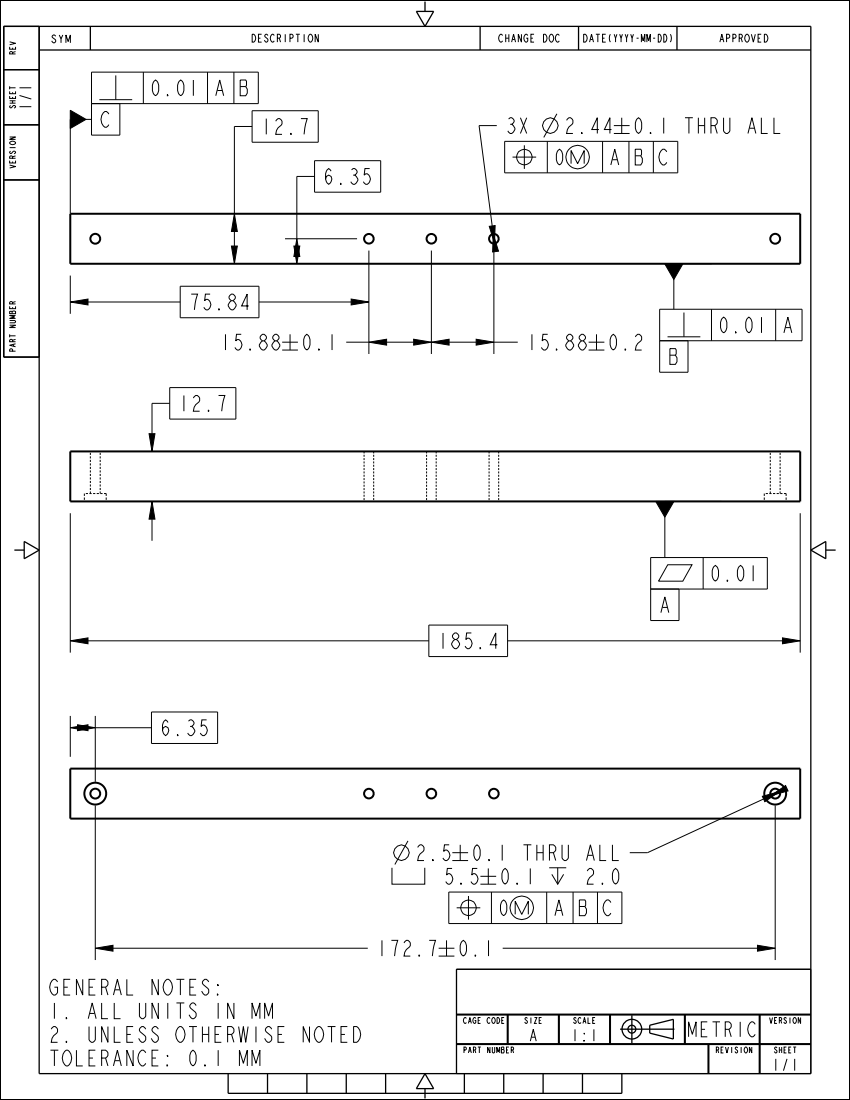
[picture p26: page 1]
SYM; DESCRIPTION; CHANGE; DOC; DATE(YYYY-MM-DD); APPROVED; 3X 2.44± 0.1 THRU ALL; PART NUMBER; REVISION; SHEET; METRIC CAGE; CODE; SIZE; SCALE; VERSION

PART NUMBER VERSION SHEET REV

0.01 | A | B

2.5± 0.1 THRU ALL

GENERAL NOTES:
1. ALL UNITS IN MM
2. UNLESS OTHERWISE NOTED
TOLERANCE: 0.1 MM

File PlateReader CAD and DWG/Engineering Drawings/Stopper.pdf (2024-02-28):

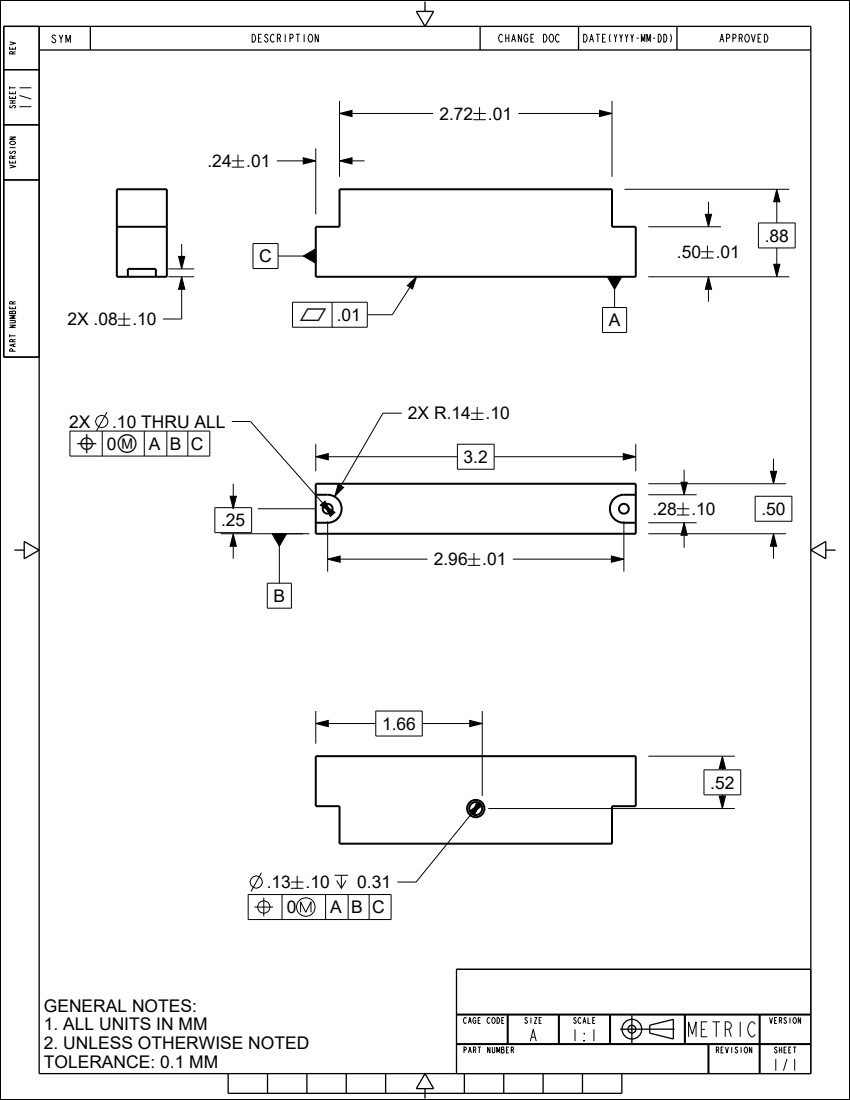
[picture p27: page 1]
SYM; DESCRIPTION; CHANGE; DOC; DATE(YYYY-MM-DD); APPROVED; PART NUMBER; REVISION; SHEET; METRIC CAGE; CODE; SIZE; SCALE; VERSION; 2X .10 THRU ALL

PART NUMBER VERSION SHEET REV

GENERAL NOTES:
1. ALL UNITS IN MM
2. UNLESS OTHERWISE NOTED
TOLERANCE: 0.1 MM

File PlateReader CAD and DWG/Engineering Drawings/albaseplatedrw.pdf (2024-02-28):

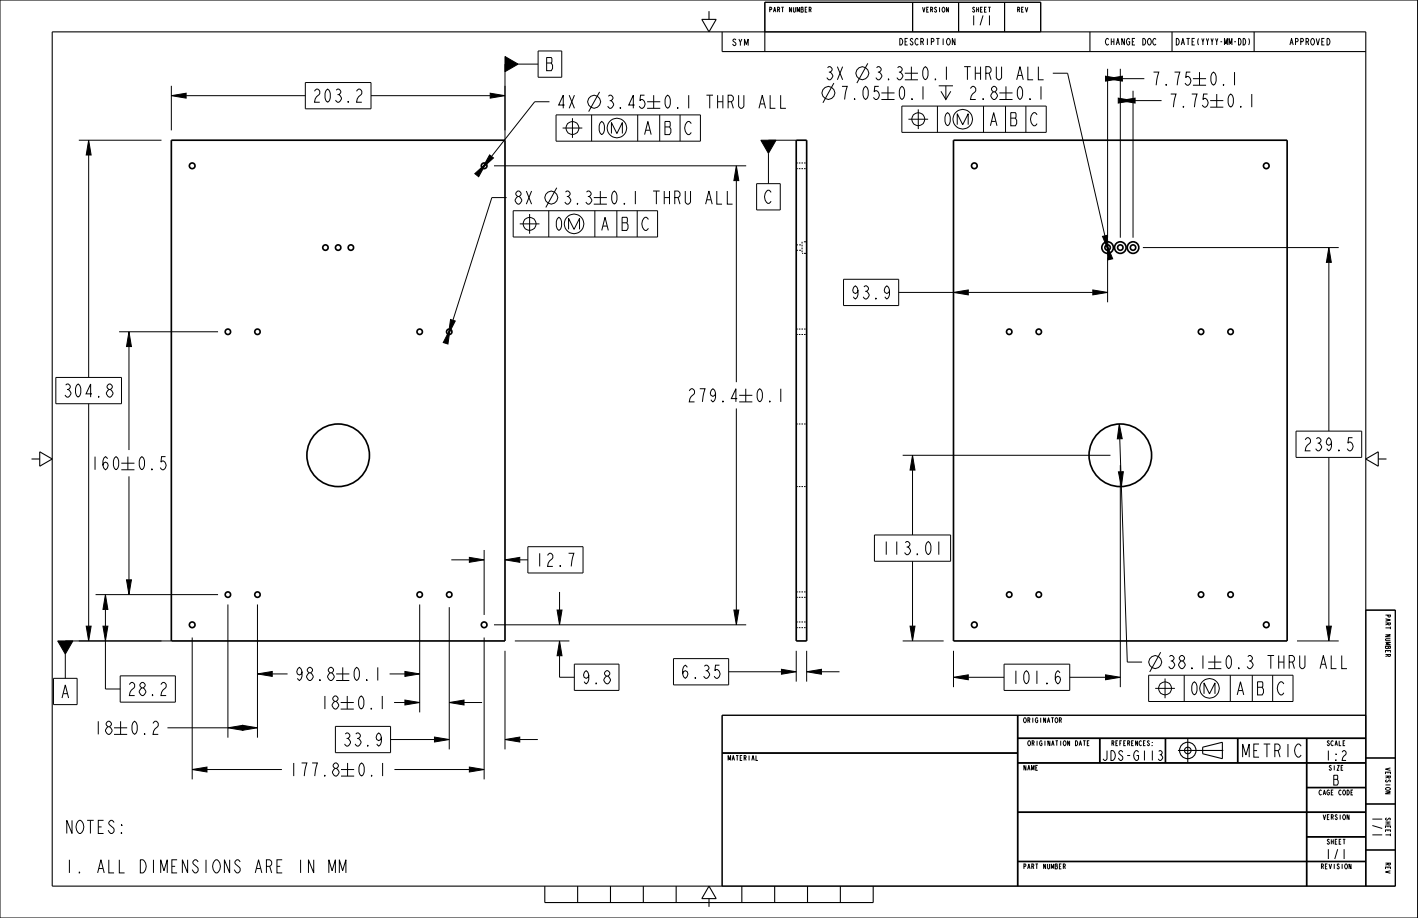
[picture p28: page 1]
SYM; DESCRIPTION; CHANGE; DOC; DATE(YYYY-MM-DD); APPROVED; 4X 3.45± 0.1 THRU ALL; 8X 3.3± 0.1 THRU ALL; 38.1± 0.3 THRU ALL; 3X 3.3± 0.1 THRU ALL; PART NUMBER; VERSION; SHEET; REV; ORIGINATOR; ORIGINATION DATE; REFERENCES:; METRIC; SCALE; MATERIAL; JDS-G113; 1:2 NAME; SIZE; B CAGE; CODE; 1/1 PART NUMBER; REVISION

PART NUMBER VERSION SHEET REV

NOTES:
1. ALL DIMENSIONS ARE IN MM

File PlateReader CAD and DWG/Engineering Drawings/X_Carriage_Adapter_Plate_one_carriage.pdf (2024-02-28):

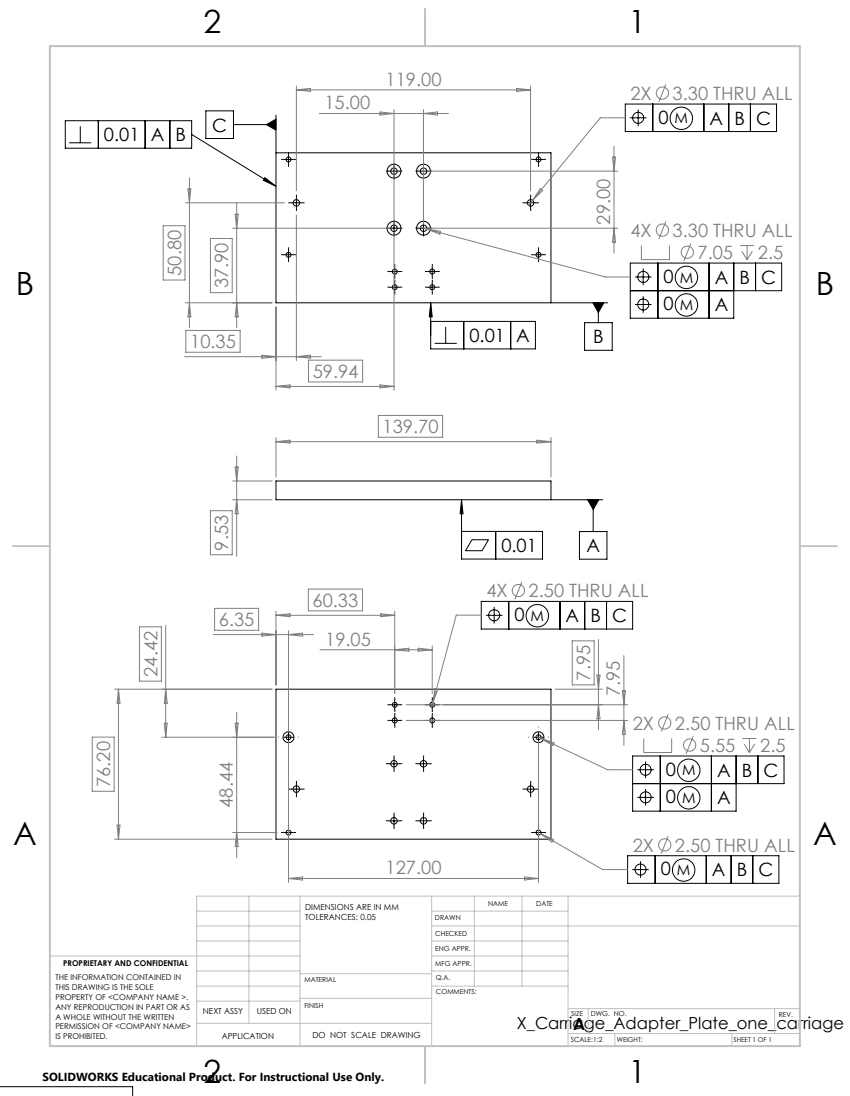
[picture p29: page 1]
2X 3.30 THRU ALL; 4X 3.30 THRU ALL 7.05 2.5; 2X 2.50 THRU ALL; 2X 2.50 THRU ALL 5.55 2.5; 4X 2.50 THRU ALL

TOLERANCES: 0.05 | | NAME | DATE DIMENSIONS ARE IN MM

DRAWN
CHECKED
ENG APPR.

PROPRIETARY AND CONFIDENTIAL THE INFORMATION CONTAINED IN THIS DRAWING IS THE SOLE PROPERTY OF <COMPANY NAME >. ANY REPRODUCTION IN PART OR AS A WHOLE WITHOUT THE WRITTEN PERMISSION OF <COMPANY NAME> IS PROHIBITED. | | | MFG APPR.

MATERIAL | Q.A.

NEXT ASSY | USED ON | FINISH

SIZE A | DWG. NO. | REV.

APPLICATION | | DO NOT SCALE DRAWING

SCALE:1:2 | WEIGHT: | SHEET 1 OF 1

SOLIDWORKS Educational Product. For Instructional Use Only.

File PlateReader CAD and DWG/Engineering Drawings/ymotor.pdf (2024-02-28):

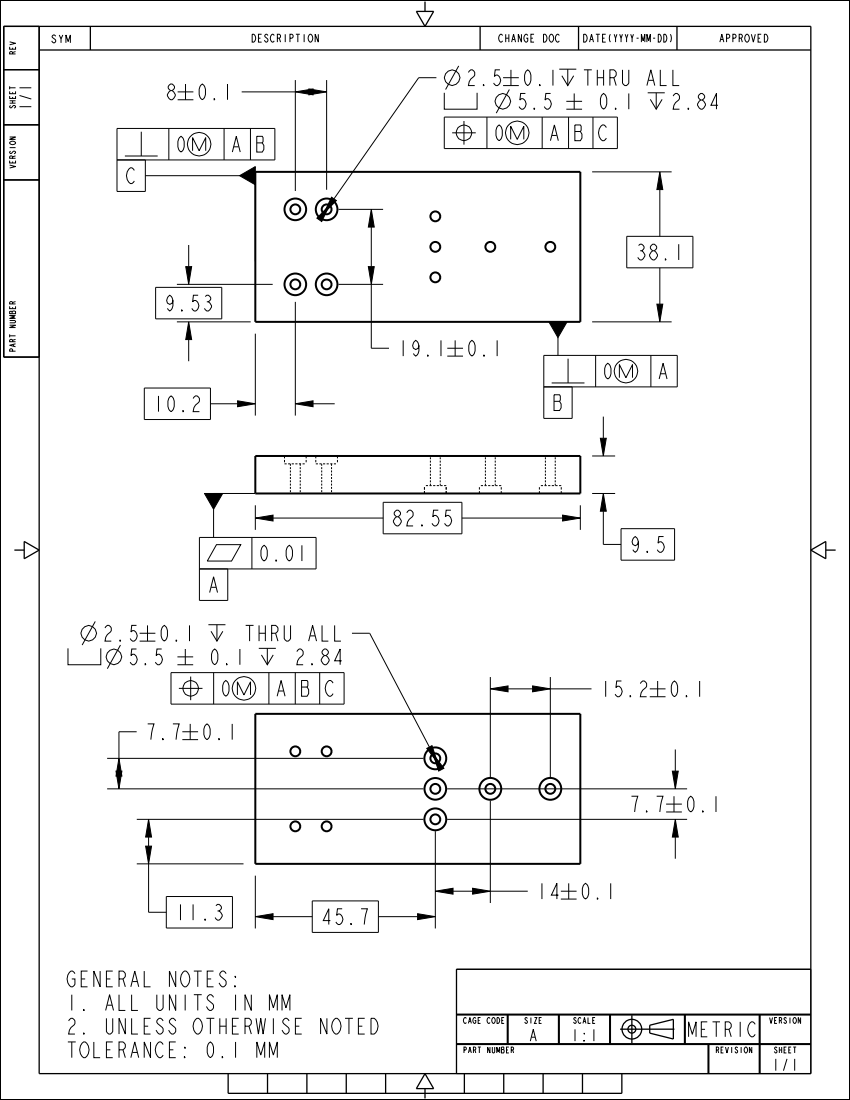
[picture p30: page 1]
SYM; DESCRIPTION; CHANGE; DOC; DATE(YYYY-MM-DD); APPROVED; THRU ALL; PART NUMBER; REVISION; SHEET; METRIC CAGE; CODE; SIZE; SCALE; VERSION; TOLERANCE: 0.1

PART NUMBER VERSION SHEET REV

GENERAL NOTES:
1. ALL UNITS IN MM
2. UNLESS OTHERWISE NOTED

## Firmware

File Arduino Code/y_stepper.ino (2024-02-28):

#include <Stepper.h>

const int stepsPerRevolution = 400;
const float stepDistance = 0.0128;
Stepper myStepper(stepsPerRevolution, 8, 9); // 8 is PUL, 9 is DIR

int currentPos = 0; 

void setup() {
    myStepper.setSpeed(1000); // Set the speed in RPM
    Serial.begin(9600); // Start serial communication
    //myStepper.step(250);
}

const long steps = mmToSteps(9);
void loop() {
    if (Serial.available() > 0) {
        Serial.println("Please enter an integer between 1 and 12:");

        // Wait for all serial data to arrive
        delay(100); 

        String inputString = Serial.readStringUntil('\n'); // Read the entire string until newline

        // Convert the input string to an integer
        int userInput = inputString.toInt(); 

        // Check if the input is not between 1 and 12
        if (userInput < 0 || userInput > 12) {
            Serial.println("Invalid input. Please enter an integer between 1 and 12.");
            return;
        }

        if (userInput == 0){
          userInput = 1;
        }
        
        int targetPos = userInput - 1; // Convert to zero-based index
        int itersToMove = targetPos - currentPos; // Calculate the relative steps to move

        runner(itersToMove, steps); // Move the stepper

        currentPos = targetPos; // Update current position

        Serial.println();
        Serial.print("You are at position: ");
        Serial.print(currentPos);
    }
}

// Function to convert millimeters to steps
long mmToSteps(long mm) {
    return 8 * round(mm / stepDistance);
}

void runner(int iterations, long steps){
    if (iterations < 0){
        steps = -steps; // Reverse direction if iterations is negative
        iterations = -iterations; // Make iterations positive
    }
  
    for (int i = 0; i < iterations; i++){
        myStepper.step(steps);
        Serial.println(i);
    }
}

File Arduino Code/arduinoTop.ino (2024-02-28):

#include <Stepper.h>

const int stepsPerRevolution = 400;  // Number of steps per revolution
const float stepDistance = 0.00396875;  // Distance per step in inches

Stepper myStepper(stepsPerRevolution, 8, 9);

void setup() {
    myStepper.setSpeed(500);
    Serial.begin(9600);
    Serial.flush();
    myStepper.step(8000);
}

const long steps = mmToSteps(1);
const int iters = 6;
void loop() {
    //Move down
    if (promptUser('y')) {
        runner(iters, -steps);
        delay(1000);
    }

    // Move up
    if (promptUser('y')) {
        runner(iters, steps);
        delay(1000);
    }
}

long mmToSteps(float mm) {
    float mmPerStep = stepDistance / 25.4;
    return round(mm / mmPerStep);
}

void runner(int iterations, long steps) {
    for (int i = 0; i < iterations; i++) {
        myStepper.step(steps);
    }
}

bool promptUser(char expectedChar) {
    Serial.print("Press '");
    Serial.print(expectedChar);
    Serial.println("' to move the stepper motor:");

    while (true) {
        if (Serial.available() > 0) {
            char receivedChar = Serial.read();
            if (receivedChar == expectedChar) {
                return true;
            }
        }
    }
}
